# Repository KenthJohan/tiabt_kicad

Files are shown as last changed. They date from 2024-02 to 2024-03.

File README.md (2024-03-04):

# TIABT

This circuit is used for controlling LEDs and measure photodiodes.

Specification
* Power input
    * 16V to 20V
    * Max 0.2A
* 8 channels current measurment
    * 10pA resolution from 1µA current offset
    * Optional 1µA current subtractor
    * Supports large range of feedback resistor in TIA
* 7 channels LED driver
    * Software controlled current
    * 0.3mA to 2.14mA, 255 steps
    * Up to 12V
    * Enable and Disable

## Board
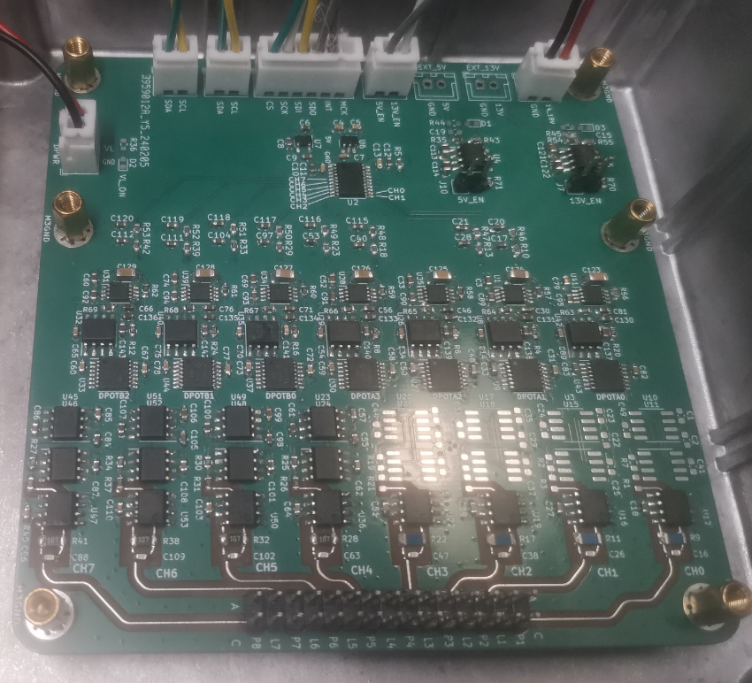
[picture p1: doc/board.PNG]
board


## Box

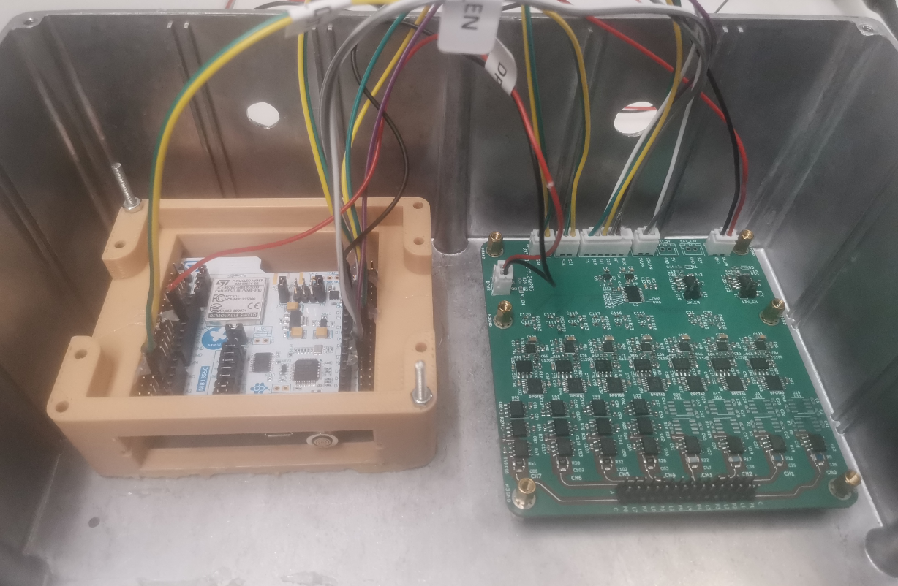
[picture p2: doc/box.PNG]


## 10pA measuement of one channel
* Feedback resistor is `100Mohm`
* Current subtractor, `1µA` 
* `1µA` plus `n*10pA`, n=1,2,3,4,5,6 steps from SMU with coaxial cable
* SMU is Keysight B2910BL

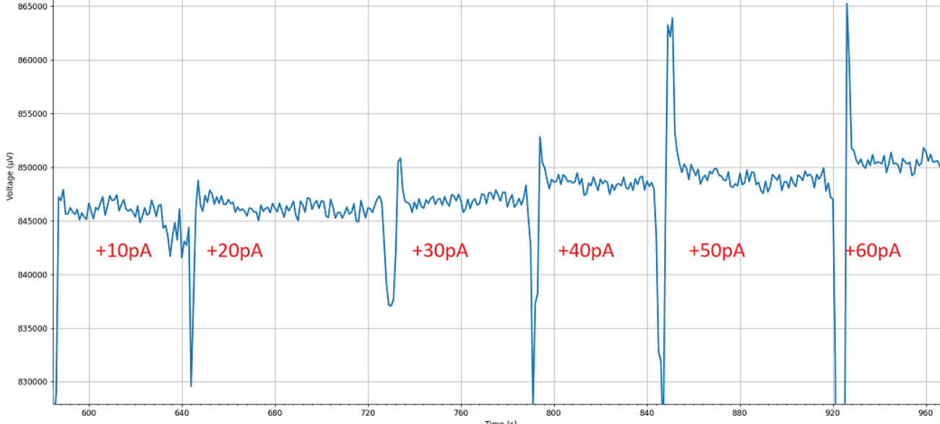
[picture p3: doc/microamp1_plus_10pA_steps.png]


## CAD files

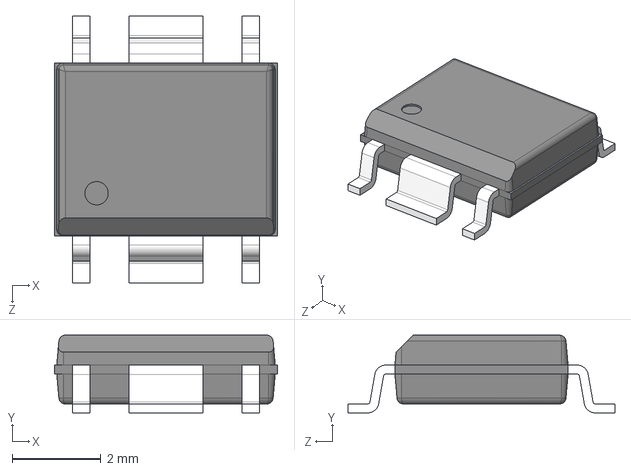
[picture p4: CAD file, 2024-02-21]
3d/HSOP-6J-6.step
5.02 x 1.75 x 6.00 mm

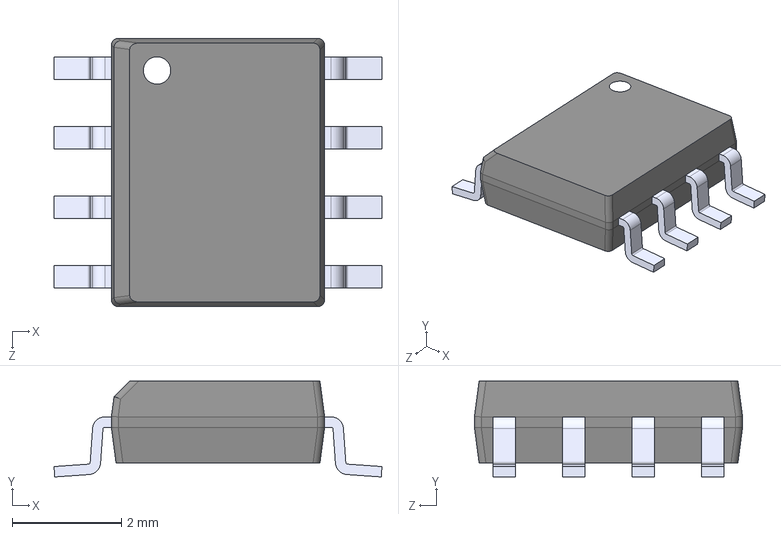
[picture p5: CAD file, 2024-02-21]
3d/OPA277UA.step
5.99 x 1.75 x 4.90 mm

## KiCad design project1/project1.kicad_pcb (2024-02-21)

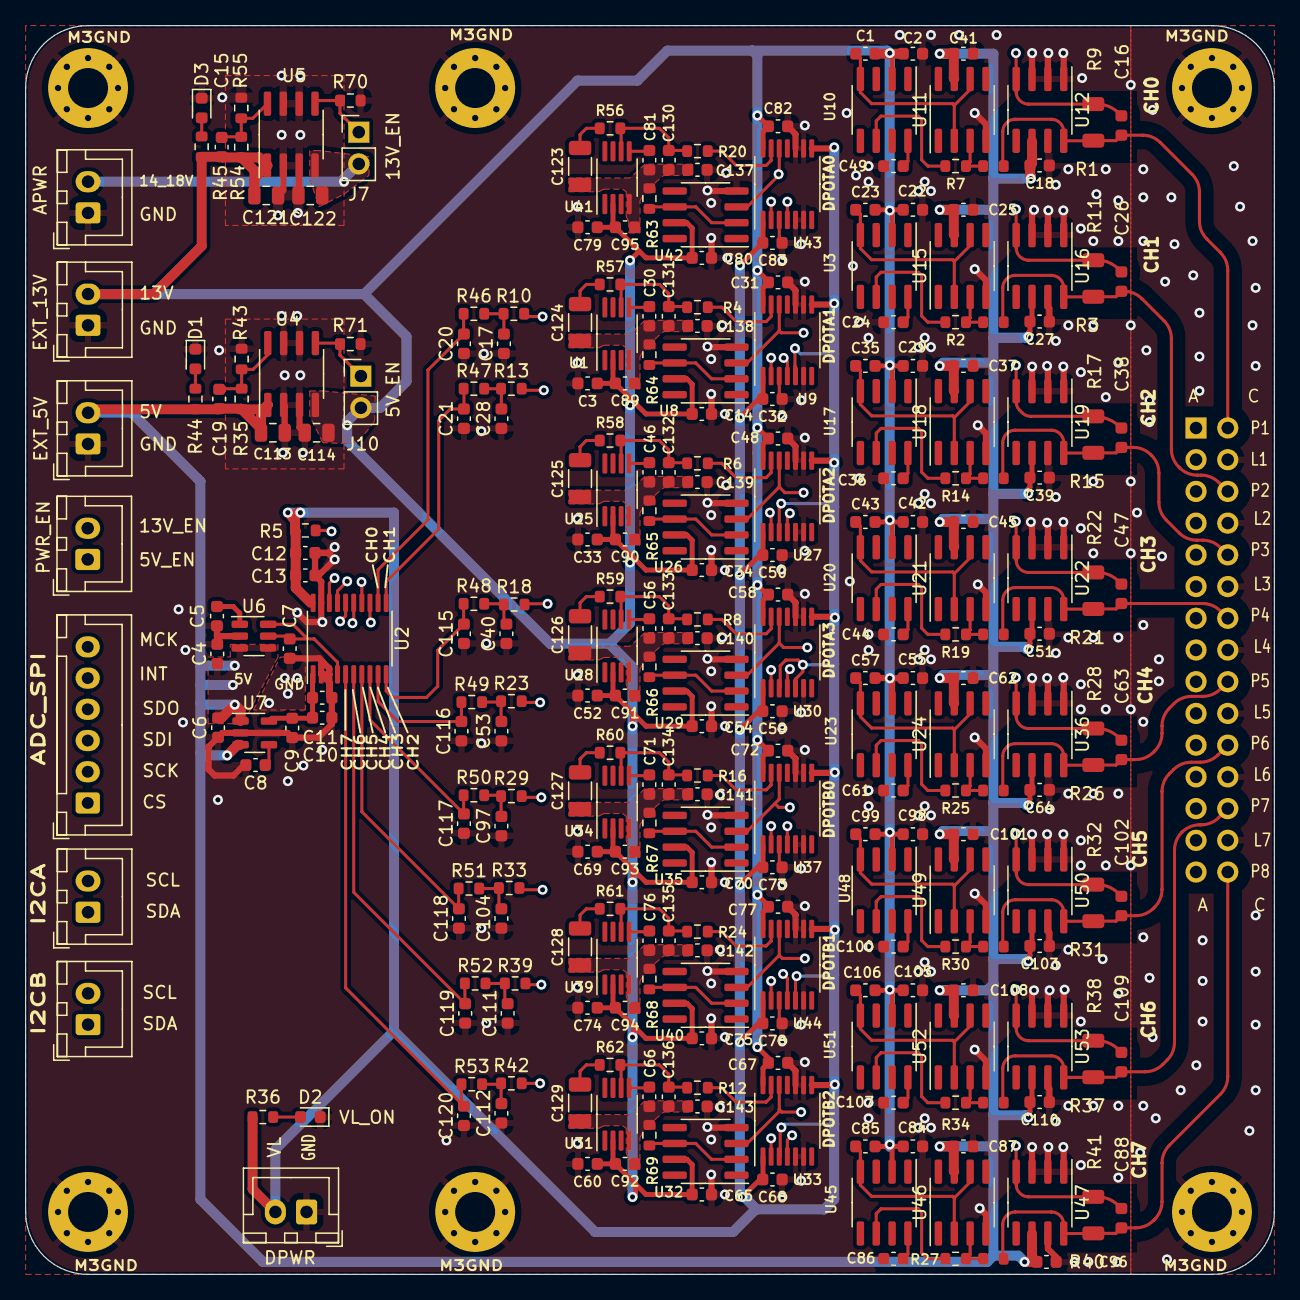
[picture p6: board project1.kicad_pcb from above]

Board: 4 copper layers, 100.0 x 100.0 mm, 299 parts (0 on the bottom side), 139 nets.

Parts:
C1, C2, C6, C22, C23, C24, C25, C29, C35, C36, C37, C41, C42, C43, C44, C45, C49, C55, C57, C61, C62, C84, C85, C86, C87, C98, C99, C100, C101, C105, C106, C107, C108: 1uF; C_0603_1608Metric
C3, C10, C12, C18, C27, C30, C33, C39, C46, C51, C52, C56, C60, C64, C66, C69, C71, C74, C76, C79, C81, C89, C90, C91, C92, C93, C94, C95, C96, C103, C110, C130, C131, C132, C133, C134, C135, C136, C137, C138, C139, C140, C141, C142, C143: 1µF; C_0603_1608Metric
C4, C5, C7, C11, C13: 0.1µF; C_0603_1608Metric
C8: 10nF; C_0603_1608Metric
C9, C17, C20, C21, C28, C40, C53, C97, C104, C111, C112, C115, C116, C117, C118, C119, C120: 2.2uF; C_0603_1608Metric
C14, C31, C32, C34, C48, C50, C54, C58, C59, C65, C67, C68, C70, C72, C73, C75, C77, C78, C80, C82, C83: 0.1μF; C_0603_1608Metric
C15, C19: 1nF; C_0603_1608Metric
C16, C26, C38, C47, C63, C88, C102, C109: 270pF; FB_C_0603_1608Metric
C113, C121: 1uF; C_0805_2012Metric
C114, C122: 4.7uF; C_0805_2012Metric
C123, C124, C125, C126, C127, C128, C129: 10µF; C_1206_3216Metric
D1, D2, D3: LED; LED_0603_1608Metric
H1, H2, H3, H4, H5, H6: MountingHole_Pad; MountingHole_3.2mm_M3_Pad_Via
J1, J3, J4, J5, J6, J8, J9: Conn_01x02_Pin; JST_XH_B2B-XH-A_1x02_P2.50mm_Vertical
J2: Conn_01x06_Pin; JST_XH_B6B-XH-A_1x06_P2.50mm_Vertical
J7, J10: Conn_01x02_Pin; PinHeader_1x02_P2.54mm_Vertical
R1, R3, R15, R21, R26, R31, R37, R40: 500K; TIA_R_0603_1608Metric
R2, R7, R14, R19, R25, R27, R30, R34: 10M; R_0603_1608Metric
R4, R6, R8, R12, R16, R20, R24: 1K; R_0603_1608Metric
R5: 10k; R_0603_1608Metric
R9, R11, R17, R22, R28, R32, R38, R41: R; FB_R_1206_3216Metric
R10, R13, R18, R23, R29, R33, R39, R42, R46, R47, R48, R49, R50, R51, R52, R53: 2.2K; R_0603_1608Metric
R35: 300k; R_0603_1608Metric
R36, R44, R45, R71: R; R_0603_1608Metric
R43: 91k; R_0603_1608Metric
R54: 360k; R_0603_1608Metric
R55: 30k; R_0603_1608Metric
R56, R57, R58, R59, R60, R61, R62, R63, R64, R65, R66, R67, R68, R69: 1; R_0603_1608Metric
R70: 200k; R_0603_1608Metric
U1, U25, U28, U31, U34, U39, U41: REF5020IDGK; MSOP-8_3x3mm_P0.65mm
U2: MCP3564-E/ST; TSSOP-20_4.4x6.5mm_P0.65mm
U3, U10, U17, U20, U23, U45, U48, U51: REF102CU; SOIC-8_3.9x4.9mm_P1.27mm
U4, U5: SOIC-8_3.9x4.9mm_P1.27mm
U6: MAX6070AAUT12+T; SOT-23-6
U7: LP2985-3.3; SOT-23-5
U8, U11, U15, U18, U21, U24, U26, U29, U32, U35, U40, U42, U46, U49, U52: OPA277UA; SOIC-8_3.9x4.9mm_P1.27mm
U9, U27, U30, U33, U37, U43, U44: MCP45HV31-ST; TSSOP-14_4.4x5mm_P0.65mm
U12, U16, U19, U22, U36, U47, U50, U53: LMP7721MA; SOIC-8_3.9x4.9mm_P1.27mm
U38: OPM_Sensor_PinHeader_2x15_P2.54mm_Vertical
U54, U55, U56, U57, U58, U59, U60: OLED_Driver_Outline
U61, U62, U63, U64, U65, U66, U67, U68: OPD_TIA_Outline

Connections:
5V: C4.1, C6.1, C18.2, C19.1, C25.2, C27.2, C37.2, C39.2, C41.2, C45.2, C51.2, C62.2, C64.2, C87.2, C96.2, C101.2, C103.2, C108.2, C110.2, C114.1, J4.2, R35.1, R44.1, U4.1 (VOUT), U6.3 (EN), U6.4 (IN), U7.1 (VIN), U7.3 (ON/~OFF), U11.7 (V+), U12.6 (V+), U15.7 (V+), U16.6 (V+), U18.7 (V+), U19.6 (V+), U21.7 (V+), U22.6 (V+), U24.7 (V+), U36.6 (V+), U46.7 (V+), U47.6 (V+), U49.7 (V+), U50.6 (V+), U52.7 (V+), U53.6 (V+)
5V_EN: J6.1, J10.1, R71.2, U4.5 (EN)
13V: C1.2, C2.2, C3.1, C14.1, C15.1, C22.2, C23.2, C29.2, C31.1, C33.1, C34.1, C35.2, C42.2, C43.2, C48.1, C52.1, C54.1, C55.2, C57.2, C58.1, C60.1, C65.1, C67.1, C69.1, C70.1, C72.1, C74.1, C75.1, C77.1, C79.1, C80.1, C82.1, C84.2, C85.2, C89.1, C90.1, C91.1, C92.1, C93.1, C94.1, C95.1, C98.2, C99.2, C105.2, C106.2, C113.1, C122.1, J5.2, J10.2, R45.1, R54.1, U1.2 (Vin), U3.2 (Vin), U4.4 (VIN), U5.1 (VOUT), U8.7 (V+), U9.14 (V+), U10.2 (Vin), U17.2 (Vin), U20.2 (Vin), U23.2 (Vin), U25.2 (Vin), U26.7 (V+), U27.14 (V+), U28.2 (Vin), U29.7 (V+), U30.14 (V+), U31.2 (Vin), U32.7 (V+), U33.14 (V+), U34.2 (Vin), U35.7 (V+), U37.14 (V+), U39.2 (Vin), U40.7 (V+), U41.2 (Vin), U42.7 (V+), U43.14 (V+), U44.14 (V+), U45.2 (Vin), U48.2 (Vin), U51.2 (Vin)
13V_EN: J6.2, J7.1, R70.2, U5.5 (EN)
/ADC_AVDD: C9.1, C10.2, C11.2, U2.1 (AVDD), U7.5 (VOUT)
/ADC_REFIN+: C7.1, U2.4 (REFIN+), U6.5 (OUTS), U6.6 (OUTF)
/OLED_driver1/OLED_8V_BUFFERED: C81.2, C95.2, C123.2, C130.2, C137.1, R63.1, U41.4 (GND)
/OLED_driver1/RELATIVE_2.048V_ABSOLTE_10V: C130.1, R20.1, R56.1, U41.6 (Vout)
/OLED_driver2/OLED_8V_BUFFERED: C30.2, C89.2, C124.2, C131.2, C138.1, R64.1, U1.4 (GND)
/OLED_driver2/RELATIVE_2.048V_ABSOLTE_10V: C131.1, R4.1, R57.1, U1.6 (Vout)
/OLED_driver3/OLED_8V_BUFFERED: C46.2, C90.2, C125.2, C132.2, C139.1, R65.1, U25.4 (GND)
/OLED_driver3/RELATIVE_2.048V_ABSOLTE_10V: C132.1, R6.1, R58.1, U25.6 (Vout)
/OLED_driver4/OLED_8V_BUFFERED: C56.2, C91.2, C126.2, C133.2, C140.1, R66.1, U28.4 (GND)
/OLED_driver4/RELATIVE_2.048V_ABSOLTE_10V: C133.1, R8.1, R59.1, U28.6 (Vout)
/OLED_driver5/OLED_8V_BUFFERED: C71.2, C93.2, C127.2, C134.2, C141.1, R67.1, U34.4 (GND)
/OLED_driver5/RELATIVE_2.048V_ABSOLTE_10V: C134.1, R16.1, R60.1, U34.6 (Vout)
/OLED_driver6/OLED_8V_BUFFERED: C76.2, C94.2, C128.2, C135.2, C142.1, R68.1, U39.4 (GND)
/OLED_driver6/RELATIVE_2.048V_ABSOLTE_10V: C135.1, R24.1, R61.1, U39.6 (Vout)
/OLED_driver7/OLED_8V_BUFFERED: C66.2, C92.2, C129.2, C136.2, C143.1, R69.1, U31.4 (GND)
/OLED_driver7/RELATIVE_2.048V_ABSOLTE_10V: C136.1, R12.1, R62.1, U31.6 (Vout)
/amp1/AMPO: C16.2, R9.2, R10.2, U12.4 (VO)
/amp1/ISRC_+IN_0.5V: R1.2, R7.1, U11.3 (+IN)
/amp1/REFGND_0.5V: C1.1, U10.4 (GND), U11.2 (-IN), U11.6 (OUTPUT)
/amp1/REF_10.5V: R7.2, U10.6 (Vout)
/amp2/AMPO: C26.2, R11.2, R13.2, U16.4 (VO)
/amp2/ISRC_+IN_0.5V: R2.1, R3.2, U15.3 (+IN)
/amp2/REFGND_0.5V: C23.1, U3.4 (GND), U15.2 (-IN), U15.6 (OUTPUT)
/amp2/REF_10.5V: R2.2, U3.6 (Vout)
/amp3/AMPO: C38.2, R17.2, R18.2, U19.4 (VO)
/amp3/ISRC_+IN_0.5V: R14.1, R15.2, U18.3 (+IN)
/amp3/REFGND_0.5V: C35.1, U17.4 (GND), U18.2 (-IN), U18.6 (OUTPUT)
/amp3/REF_10.5V: R14.2, U17.6 (Vout)
/amp4/AMPO: C47.2, R22.2, R23.2, U22.4 (VO)
/amp4/ISRC_+IN_0.5V: R19.1, R21.2, U21.3 (+IN)
/amp4/REFGND_0.5V: C43.1, U20.4 (GND), U21.2 (-IN), U21.6 (OUTPUT)
/amp4/REF_10.5V: R19.2, U20.6 (Vout)
/amp5/AMPO: C63.2, R28.2, R29.2, U36.4 (VO)
/amp5/ISRC_+IN_0.5V: R25.1, R26.2, U24.3 (+IN)
/amp5/REFGND_0.5V: C57.1, U23.4 (GND), U24.2 (-IN), U24.6 (OUTPUT)
/amp5/REF_10.5V: R25.2, U23.6 (Vout)
/amp6/AMPO: C102.2, R32.2, R33.2, U50.4 (VO)
/amp6/ISRC_+IN_0.5V: R30.1, R31.2, U49.3 (+IN)
/amp6/REFGND_0.5V: C99.1, U48.4 (GND), U49.2 (-IN), U49.6 (OUTPUT)
/amp6/REF_10.5V: R30.2, U48.6 (Vout)
/amp7/AMPO: C109.2, R38.2, R39.2, U53.4 (VO)
/amp7/ISRC_+IN_0.5V: R34.1, R37.2, U52.3 (+IN)
/amp7/REFGND_0.5V: C106.1, U51.4 (GND), U52.2 (-IN), U52.6 (OUTPUT)
/amp7/REF_10.5V: R34.2, U51.6 (Vout)
/amp8/AMPO: C88.2, R41.2, R42.2, U47.4 (VO)
/amp8/ISRC_+IN_0.5V: R27.1, R40.2, U46.3 (+IN)
/amp8/REFGND_0.5V: C85.1, U45.4 (GND), U46.2 (-IN), U46.6 (OUTPUT)
/amp8/REF_10.5V: R27.2, U45.6 (Vout)
ADC_CH0: C20.2, R46.1, U2.12 (CH7)
ADC_CH1: C21.2, R47.1, U2.11 (CH6)
ADC_CH2: C115.2, R48.1, U2.10 (CH5)
ADC_CH3: C116.2, R49.1, U2.9 (CH4)
ADC_CH4: C117.2, R50.1, U2.8 (CH3)
ADC_CH5: C118.2, R51.1, U2.7 (CH2)
ADC_CH6: C119.2, R52.1, U2.6 (CH1)
ADC_CH7: C120.2, R53.1, U2.5 (CH0)
ADC_CS: J2.1, U2.13 (*CS)
ADC_INT: J2.5, R5.2, U2.17 (*IRQ/MDAT)
ADC_MCK: J2.6, U2.18 (MCLKIN)
ADC_SCK: J2.2, U2.14 (SCK)
ADC_SDI: J2.3, U2.15 (SDI)
ADC_SDO: J2.4, U2.16 (SDO)
BATT_14V_24V: C121.1, J1.2, J7.2, U5.4 (VIN)
DPOT_A_SCL: J8.2, U9.2 (SCL), U27.2 (SCL), U30.2 (SCL), U43.2 (SCL)
DPOT_A_SDA: J8.1, U9.4 (SDA), U27.4 (SDA), U30.4 (SDA), U43.4 (SDA)
DPOT_B_SCL: J9.2, U33.2 (SCL), U37.2 (SCL), U44.2 (SCL)
DPOT_B_SDA: J9.1, U33.4 (SDA), U37.4 (SDA), U44.4 (SDA)
GND: C2.1, C3.2, C4.2, C5.2, C6.2, C7.2, C8.2, C9.2, C10.1, C11.1, C12.2, C13.2, C14.2, C17.1, C18.1, C20.1, C21.1, C22.1, C24.1, C25.1, C27.1, C28.1, C29.1, C31.2, C32.2, C33.2, C34.2, C36.1, C37.1, C39.1, C40.1, C41.1, C42.1, C44.1, C45.1, C48.2, C49.1, C50.2, C51.1, C52.2, C53.1, C54.2, C55.1, C58.2, C59.2, C60.2, C61.1, C62.1, C64.1, C65.2, C67.2, C68.2, C69.2, C70.2, C72.2, C73.2, C74.2, C75.2, C77.2, C78.2, C79.2, C80.2, C82.2, C83.2, C84.1, C86.1, C87.1, C96.1, C97.1, C98.1, C100.1, C101.1, C103.1, C104.1, C105.1, C107.1, C108.1, C110.1, C111.1, C112.1, C113.2, C114.2, C115.1, C116.1, C117.1, C118.1, C119.1, C120.1, C121.2, C122.2, C137.2, C138.2, C139.2, C140.2, C141.2, C142.2, C143.2, D1.1 (K), D2.1 (K), D3.1 (K), H1.1, H2.1, H3.1, H4.1, H5.1, H6.1, J1.1, J3.1, J4.1, J5.1, R43.2, R55.2, R70.1, R71.1, U2.2 (AGND), U2.3 (REFIN-), U2.19 (DGND), U4.2 (GND), U4.3 (GND), U4.6 (GND), U4.7 (GND), U5.2 (GND), U5.3 (GND), U5.6 (GND), U5.7 (GND), U6.2 (GND), U7.2 (GND), U8.4 (V-), U9.3 (A1), U9.6 (~WLAT), U9.9 (DGND), U9.10 (V-), U11.4 (V-), U12.1 (IN+), U12.2 (NC), U12.3 (V-), U12.7 (NC), U15.4 (V-), U16.1 (IN+), U16.2 (NC), U16.3 (V-), U16.7 (NC), U18.4 (V-), U19.1 (IN+), U19.2 (NC), U19.3 (V-), U19.7 (NC), U21.4 (V-), U22.1 (IN+), U22.2 (NC), U22.3 (V-), U22.7 (NC), U24.4 (V-), U26.4 (V-), U27.5 (A0), U27.6 (~WLAT), U27.9 (DGND), U27.10 (V-), U29.4 (V-), U30.6 (~WLAT), U30.9 (DGND), U30.10 (V-), U32.4 (V-), U33.5 (A0), U33.6 (~WLAT), U33.9 (DGND), U33.10 (V-), U35.4 (V-), U36.1 (IN+), U36.2 (NC), U36.3 (V-), U36.7 (NC), U37.3 (A1), U37.5 (A0), U37.6 (~WLAT), U37.9 (DGND), U37.10 (V-), U38.1 (OPD1_ANODE), U38.4 (OLED1_CATHODE), U38.5 (OPD2_ANODE), U38.8 (OLED2_CATHODE), U38.9 (OPD3_ANODE), U38.12 (OLED3_CATHODE), U38.13 (OPD4_ANODE), U38.16 (OLED4_CATHODE), U38.17 (OPD5_ANODE), U38.20 (OLED5_CATHODE), U38.21 (OPD6_ANODE), U38.24 (OLED6_CATHODE), U38.25 (OPD7_ANODE), U38.28 (OLED7_CATHODE), U38.29 (OPD8_ANODE), U40.4 (V-), U42.4 (V-), U43.3 (A1), U43.5 (A0), U43.6 (~WLAT), U43.9 (DGND), U43.10 (V-), U44.3 (A1), U44.6 (~WLAT), U44.9 (DGND), U44.10 (V-), U46.4 (V-), U47.1 (IN+), U47.2 (NC), U47.3 (V-), U47.7 (NC), U49.4 (V-), U50.1 (IN+), U50.2 (NC), U50.3 (V-), U50.7 (NC), U52.4 (V-), U53.1 (IN+), U53.2 (NC), U53.3 (V-), U53.7 (NC)
unnamed: C17.2, R10.1, R46.2
unnamed: C28.2, R13.1, R47.2
unnamed: C40.2, R18.1, R48.2
unnamed: C53.2, R23.1, R49.2
unnamed: C97.2, R29.1, R50.2
unnamed: C104.2, R33.1, R51.2
unnamed: C111.2, R39.1, R52.2
unnamed: C112.2, R42.1, R53.2
unnamed: C123.1, R56.2
unnamed: C124.1, R57.2
unnamed: C125.1, R58.2
unnamed: C126.1, R59.2
unnamed: C127.1, R60.2
unnamed: C128.1, R61.2
unnamed: C129.1, R62.2
unnamed: D1.2 (A), R44.2
unnamed: D2.2 (A), R36.2
unnamed: D3.2 (A), R45.2
unnamed: C30.1, U1.5 (Trim/NR)
unnamed: C24.2, U3.8 (NR)
unnamed: C19.2, R35.2, R43.1, U4.8 (ADJ)
unnamed: C15.2, R54.2, R55.1, U5.8 (ADJ)
unnamed: C5.1, U6.1 (FILTER)
unnamed: C8.1, U7.4 (BP)
unnamed: R64.2, U8.2 (-IN), U8.6 (OUTPUT)
unnamed: R4.2, U9.13 (P0A)
unnamed: C49.2, U10.8 (NR)
unnamed: C36.2, U17.8 (NR)
unnamed: C44.2, U20.8 (NR)
unnamed: C61.2, U23.8 (NR)
unnamed: C46.1, U25.5 (Trim/NR)
unnamed: R65.2, U26.2 (-IN), U26.6 (OUTPUT)
unnamed: R6.2, U27.13 (P0A)
unnamed: C56.1, U28.5 (Trim/NR)
unnamed: R66.2, U29.2 (-IN), U29.6 (OUTPUT)
unnamed: R8.2, U30.13 (P0A)
unnamed: C66.1, U31.5 (Trim/NR)
unnamed: R69.2, U32.2 (-IN), U32.6 (OUTPUT)
unnamed: R12.2, U33.13 (P0A)
unnamed: C71.1, U34.5 (Trim/NR)
unnamed: R67.2, U35.2 (-IN), U35.6 (OUTPUT)
unnamed: R16.2, U37.13 (P0A)
unnamed: C76.1, U39.5 (Trim/NR)
unnamed: R68.2, U40.2 (-IN), U40.6 (OUTPUT)
unnamed: C81.1, U41.5 (Trim/NR)
unnamed: R63.2, U42.2 (-IN), U42.6 (OUTPUT)
unnamed: R20.2, U43.13 (P0A)
unnamed: R24.2, U44.13 (P0A)
unnamed: C86.2, U45.8 (NR)
unnamed: C100.2, U48.8 (NR)
unnamed: C107.2, U51.8 (NR)
OLED1: U38.3 (OLED1_ANODE), U42.3 (+IN), U43.12 (P0W)
OLED2: U8.3 (+IN), U9.12 (P0W), U38.7 (OLED2_ANODE)
OLED3: U26.3 (+IN), U27.12 (P0W), U38.11 (OLED3_ANODE)
OLED4: U29.3 (+IN), U30.12 (P0W), U38.15 (OLED4_ANODE)
OLED5: U35.3 (+IN), U37.12 (P0W), U38.19 (OLED5_ANODE)
OLED6: U38.23 (OLED6_ANODE), U40.3 (+IN), U44.12 (P0W)
OLED7: U32.3 (+IN), U33.12 (P0W), U38.27 (OLED7_ANODE)
OPD1_CATHODE: C16.1, R1.1, R9.1, U12.8 (IN-), U38.2 (OPD1_CATHODE)
OPD2_CATHODE: C26.1, R3.1, R11.1, U16.8 (IN-), U38.6 (OPD2_CATHODE)
OPD3_CATHODE: C38.1, R15.1, R17.1, U19.8 (IN-), U38.10 (OPD3_CATHODE)
OPD4_CATHODE: C47.1, R21.1, R22.1, U22.8 (IN-), U38.14 (OPD4_CATHODE)
OPD5_CATHODE: C63.1, R26.1, R28.1, U36.8 (IN-), U38.18 (OPD5_CATHODE)
OPD6_CATHODE: C102.1, R31.1, R32.1, U38.22 (OPD6_CATHODE), U50.8 (IN-)
OPD7_CATHODE: C109.1, R37.1, R38.1, U38.26 (OPD7_CATHODE), U53.8 (IN-)
OPD8_CATHODE: C88.1, R40.1, R41.1, U38.30 (OPD8_CATHODE), U47.8 (IN-)
VL: C12.1, C13.1, C32.1, C50.1, C59.1, C68.1, C73.1, C78.1, C83.1, J3.2, R5.1, R36.1, U2.20 (DVDD), U9.1 (VL), U9.5 (A0), U9.8 (~SHDN), U27.1 (VL), U27.3 (A1), U27.8 (~SHDN), U30.1 (VL), U30.3 (A1), U30.5 (A0), U30.8 (~SHDN), U33.1 (VL), U33.3 (A1), U33.8 (~SHDN), U37.1 (VL), U37.8 (~SHDN), U43.1 (VL), U43.8 (~SHDN), U44.1 (VL), U44.5 (A0), U44.8 (~SHDN)
